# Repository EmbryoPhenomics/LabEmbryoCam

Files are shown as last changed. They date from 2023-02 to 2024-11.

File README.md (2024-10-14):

# LabEmbryoCam

This is the Github repository for the software that runs a LabEmbryoCam.

For more information about this technology, please visit: 

* User guides and background: www.phenomyx.co.uk 
* Hardware files: https://doi.org/10.5281/zenodo.13328175.



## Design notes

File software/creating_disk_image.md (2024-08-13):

# Guide for creating a new disk image

Download a raspbian lite image from the official website (https://www.raspberrypi.com/software/operating-systems/), latest version compatible with the LEC software is 32 or 64 bit BullsEye. 

Once you have flashed an SD card with a rapsbian lite image and completed the initial setup on a raspberry pi, follow the steps outlined here: https://github.com/TheMaroonHatHacker/gnomeforpi. This will set up Gnome on the raspbian OS, providing us a Gnome desktop environment and a virtual keyboard for use with the touchscreen that comes each LEC system. To enable the virtual keyboard, simply navigate to the accessibility settings and enable virtual keyboard.

Next, you can download the LEC software via the current GitHub repository, and subsequently you can install the required dependencies for the LEC software via `pip3 install -r requirements.txt`. Once this step has completed the image should be fully set up. 

To set up the desktop icon, please see `setup_desktop_icon.md` in this repository.

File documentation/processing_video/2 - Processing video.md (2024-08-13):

# 2 - Processing video produced by the LEC instrument

We provide a number of different scripts for viewing and processing the video produced by the LEC instrument:

### Viewers

- **examples/timepoint_viewer.py**
	A simple script for scrolling through video of a single timepoint from an individual subject.
- **examples/multi-timepoint_viewer.py**
	A script for viewing the first image from multiple videos of the same individual. 

### Processing

- **examples/compile_videos.py**
	Script to compile multiple videos of each individual into a single video file per individual.
- **examples/first_frame_compile.py**
	Script to retrieve the first frame of each video for each individual in your experiment, and compiling them into timelapse video files for each individual. 

*Note that these scripts are not a prerequisite for analysing your footage.*

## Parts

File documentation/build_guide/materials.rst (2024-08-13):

.. raw:: html

 <iframe src="https://plymouth222.autodesk360.com/shares/public/SH35dfcQT936092f0e43a8cc5597dfc66965?mode=embed" width="640" height="480" allowfullscreen="true" webkitallowfullscreen="true" mozallowfullscreen="true"  frameborder="0"></iframe>

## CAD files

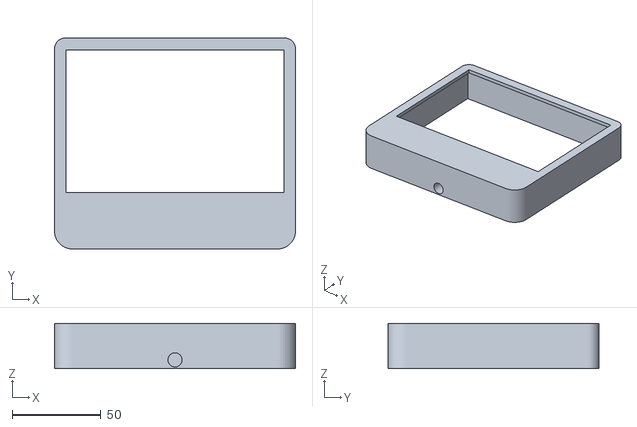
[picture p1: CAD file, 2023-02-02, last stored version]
hardware/STLs/humidification_chamber_main.stl
136.0 x 119.0 x 25.5

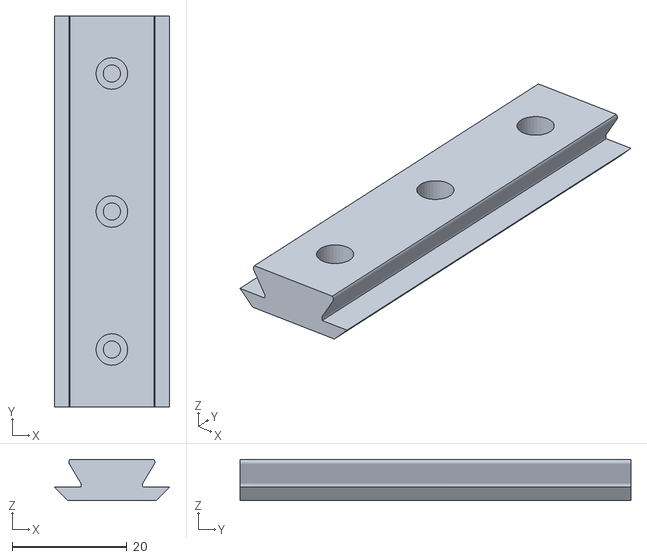
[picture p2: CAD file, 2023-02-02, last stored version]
hardware/STLs/z_carriage_assembly_light_insert.stl
20.0 x 68.0 x 7.16

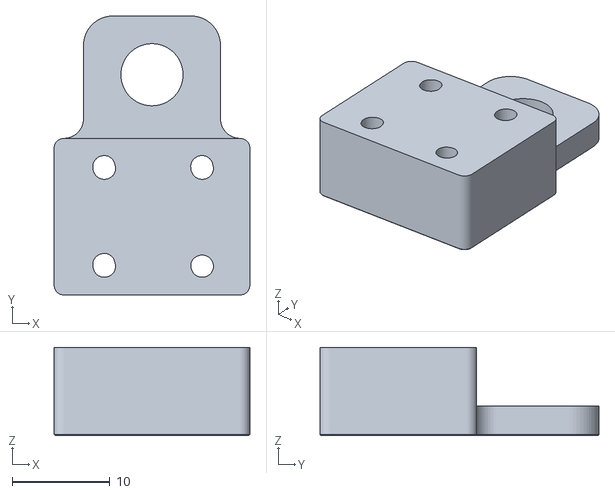
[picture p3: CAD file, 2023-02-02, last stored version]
hardware/STLs/z_carriage_assembly_camera_tripod_adapter.stl
20.0 x 28.5 x 9.00

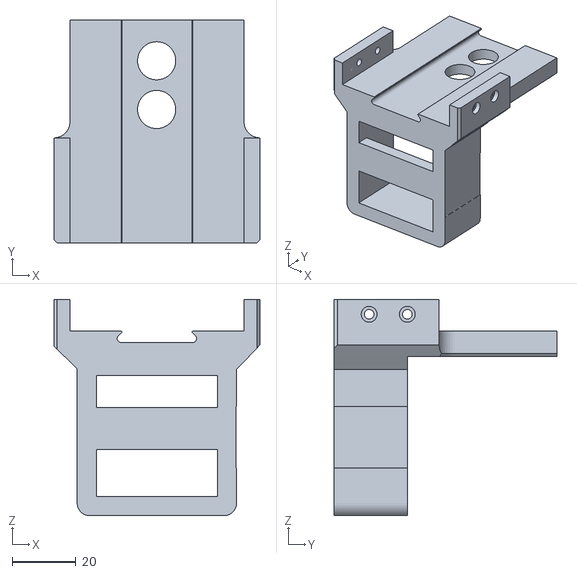
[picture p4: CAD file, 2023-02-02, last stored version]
hardware/STLs/z_carriage_assembly_camera_mount.stl
64.7 x 70.0 x 68.0

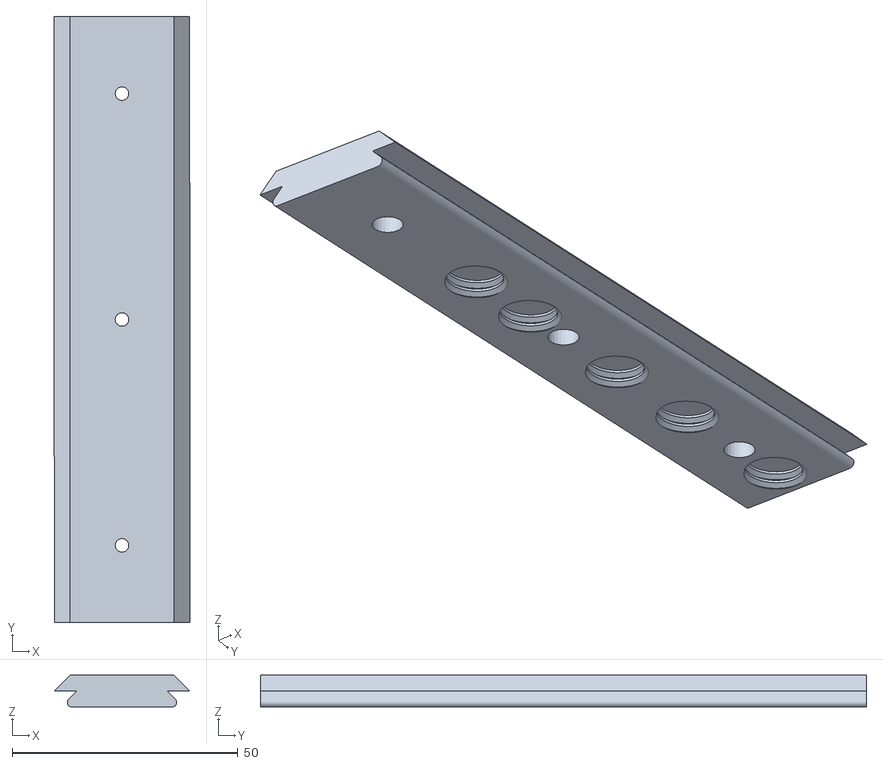
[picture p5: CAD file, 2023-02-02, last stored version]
hardware/STLs/z_carriage_assembly_optics_insert.stl
30.0 x 134.2 x 7.07

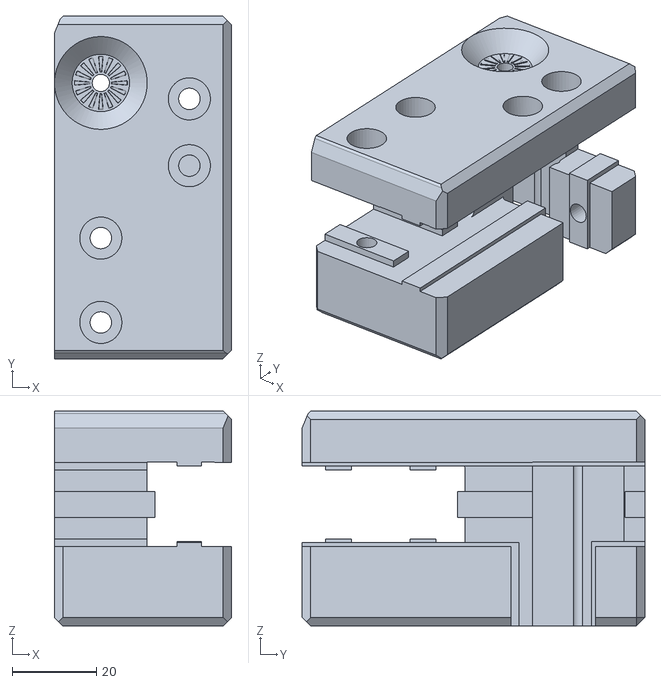
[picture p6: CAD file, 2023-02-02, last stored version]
hardware/STLs/back_motion_corner_mainbody_left.stl
42.0 x 81.3 x 51.0

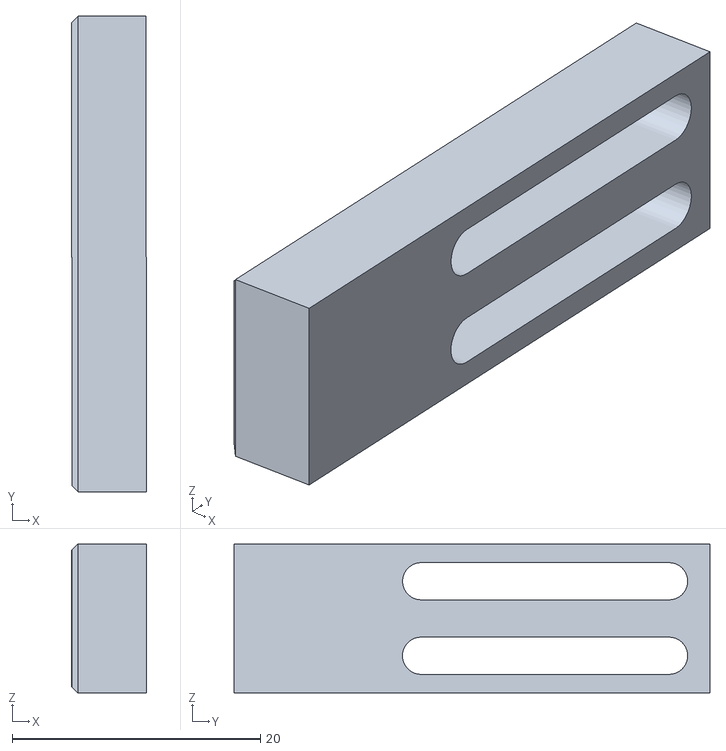
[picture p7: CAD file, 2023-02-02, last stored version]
hardware/STLs/z_carriage_assembly_limit_trigger.stl
6.00 x 38.3 x 12.0

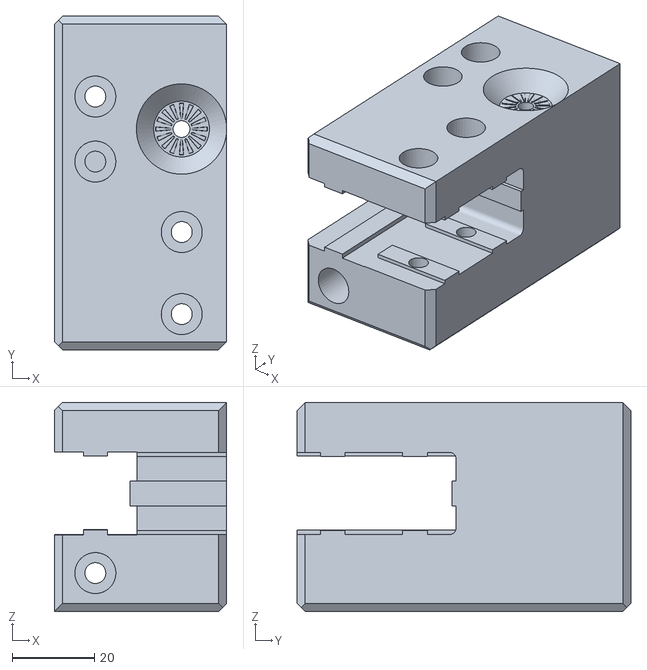
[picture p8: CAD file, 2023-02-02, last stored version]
hardware/STLs/back_motion_corner_mainbody_right.stl
42.0 x 81.4 x 51.0

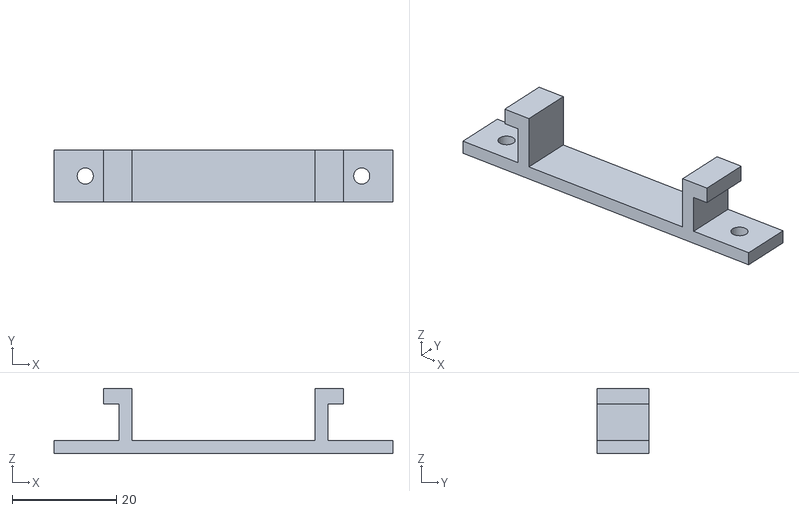
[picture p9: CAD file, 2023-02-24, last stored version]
hardware/STLs/cable vibration dampener bottom.stl
65.0 x 10.0 x 12.5

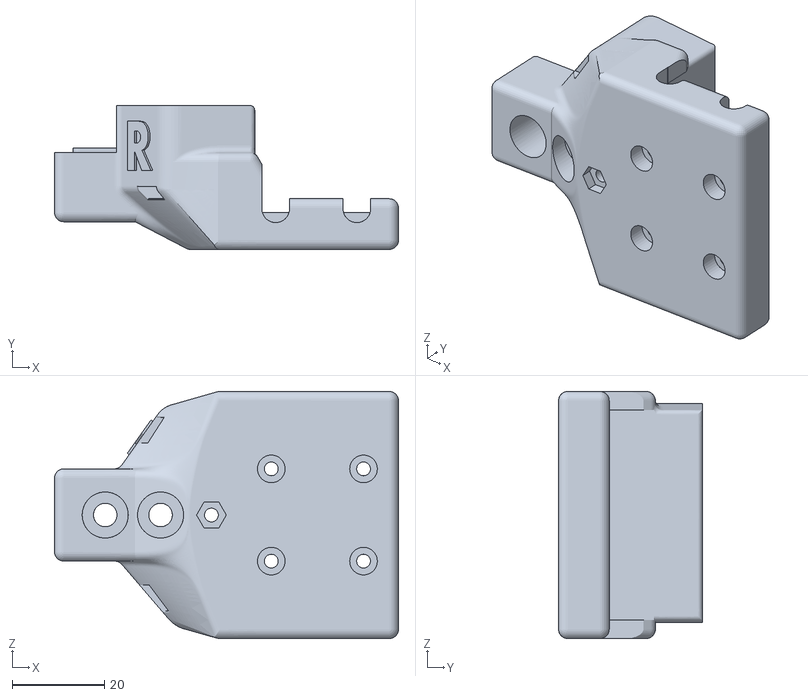
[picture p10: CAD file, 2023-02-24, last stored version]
hardware/STLs/y_mount_big_r.stl
74.6 x 31.2 x 53.6

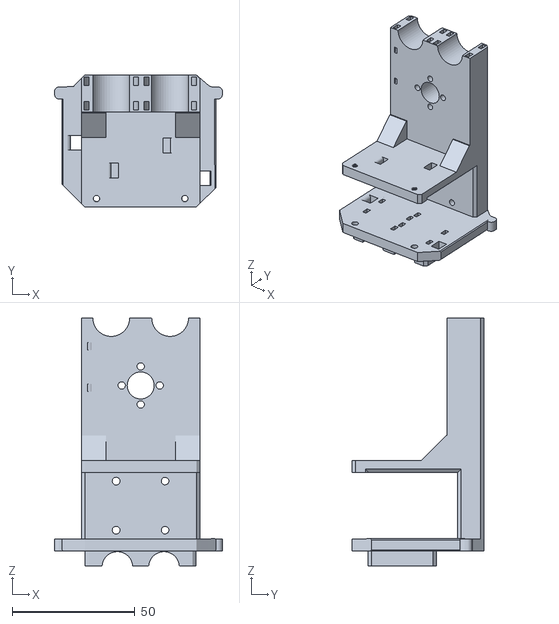
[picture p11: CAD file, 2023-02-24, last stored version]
hardware/STLs/z_carriage_rail_mount.stl
68.5 x 53.8 x 101.1

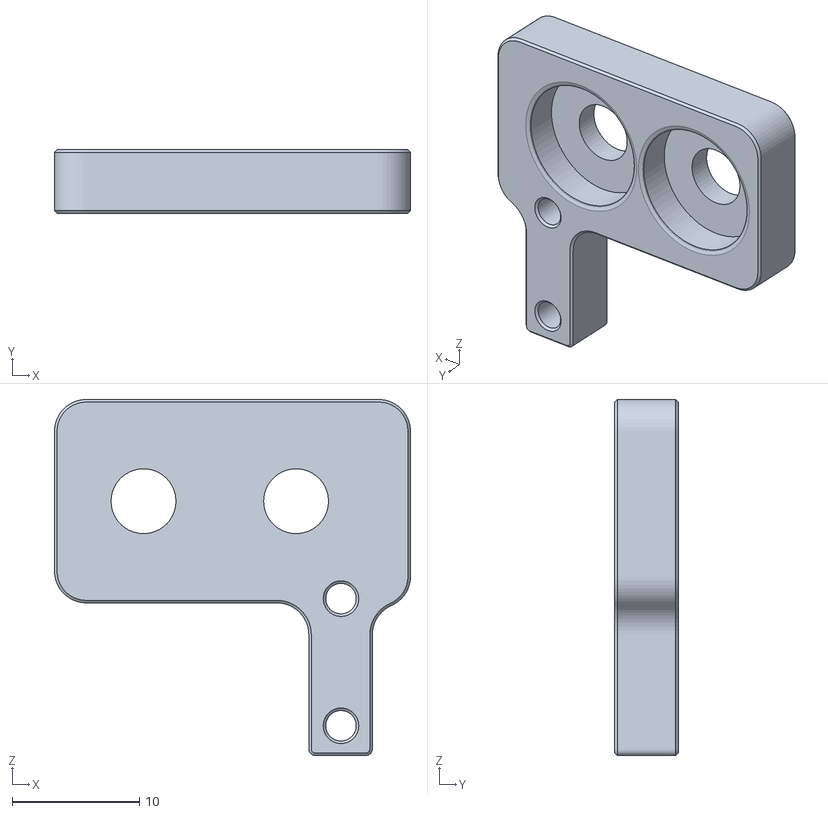
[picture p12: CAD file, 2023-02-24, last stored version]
hardware/STLs/y_mount_r_limit_switch_holder.stl
28.0 x 5.00 x 28.0

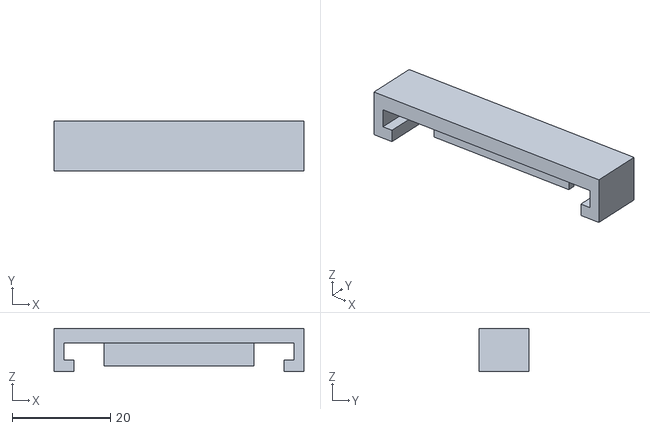
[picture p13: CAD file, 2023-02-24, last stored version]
hardware/STLs/cable vibration_dampener top.stl
51.0 x 10.2 x 8.80

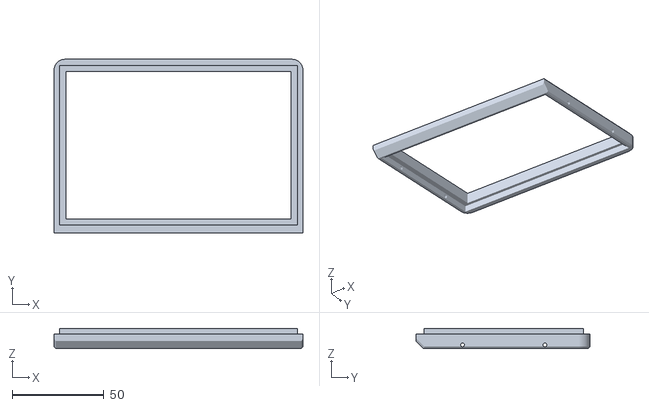
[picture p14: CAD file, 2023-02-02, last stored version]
hardware/STLs/humidification_chamber_lid.stl
136.0 x 94.8 x 11.0

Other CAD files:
hardware/STLs/y_mount_big_l.stl
hardware/STLs/z_carriage_light_carrier.stl
hardware/STLs/z_carriage_light_slider.stl
hardware/STLs/front_corner_left_bottom.stl
hardware/STLs/back_corner_knob(2).stl
hardware/STLs/back_motion_corner_left_smallbody.stl
hardware/STLs/back_motion_corner_right_smallbody.stl
hardware/STLs/bottom_corner_bracket(2).stl
hardware/STLs/bottom_corner_bracket_mirror(2).stl
hardware/STLs/electronics_SSD_mount.stl
hardware/STLs/electronics_atx_power_mount.stl
hardware/STLs/electronics_dual_arduino_mount_extended.stl
hardware/STLs/electronics_minitronics_fan fan_support(mirror)(2).stl
hardware/STLs/electronics_minitronics_fan support(2).stl
hardware/STLs/electronics_minitronics_mounting_bracket.stl
hardware/STLs/electronics_raspberry_pi_mount.stl
hardware/STLs/feet_leafspring(4).stl
hardware/STLs/front_corner_left_bottom_small.stl
hardware/STLs/front_corner_left_top.stl
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

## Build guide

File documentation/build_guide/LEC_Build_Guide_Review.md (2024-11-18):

# LabEmbryoCam Build Guide

**An opensource platform for automated measurement of developing animals**

***The LabEmbryoCam is a project originating with the EmbryoPhenomics research group at the University of Plymouth, UK. It has been made possible by support from UKRI, NERC, BBSRC and Plymouth Science Park***.

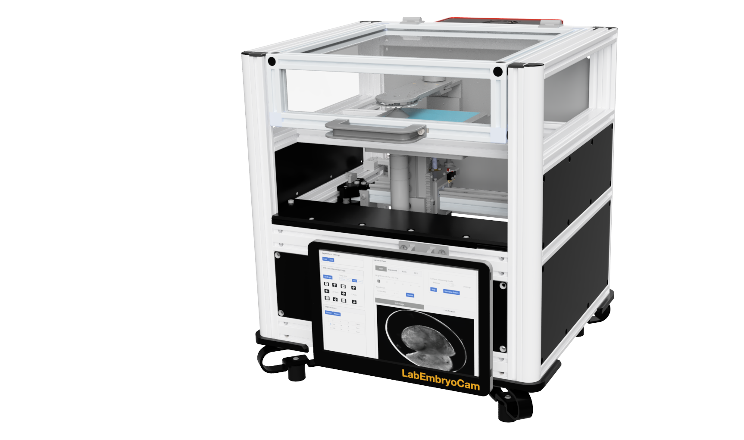
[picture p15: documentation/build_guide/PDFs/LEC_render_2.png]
Frame
 

-----------------
### 1.0 BACKGROUND
-----------------

The LabEmbryoCam provides:

* Automated movement of a camera and lighting in the X, Y and Z direction, over prolonged periods making it well suited to recording the process of embryonic development in aquatic animals.
* A custom user interface for easy setup of experiments, within a multiwell plate format, but also has sufficient flexibility for other culture formats - petri dishes, or even custom culture solutions.
* Incorporates an optional humifidification chamber to significantly reduce evaportation thereby solving one of the key challenges of long term timelapse imaging of aquatic animals.
* Vibration dampening addressing vibration, the enemy of timelapse imaging. 
* LabEmbryoCam incorporates sorbothene feet, 3D printed leafsprings and cable dampeners to minimise its effects on your imaging.
* A low cost, modular and versatile phenotyping platform taking advantage of 3D printed parts, single board computers, microcontrollers, stepper motors and lower cost cameras and lenses.
* Hackability this is an active project - if in doubt about any aspect of this instrument and its suitability to your activities, just ask.

**The LabEmbryoCam consists of both hardware and software, and the process of building both is described in the following series of pages.**

**Required Materials**

Building a LabEmbryoCam requires a range of mechnical and electrical parts, and 3D printed parts. 

* [**Components Required**](bom.md)

* [**Fixings required**](BOM_fixings.md)

The LabEmbryoCam is built using commonly available and low-cost consumer electronics, mechanical parts and 3D printed parts. Links and prices are provided as a guide, but prices vary and there is also significant scope for changing components, or suppliers due to availability, price, or user requirements.

A significant assortment of screws, nuts and washers are required to build a LabEmbryoCam (Bill of materials for fixings in **Required Materials**. To simplify the process of sourcing these parts, a kit of the required fixings can be bought here: https://www.modelfixings.co.uk/embryophenomics.htm (note this kit is not completely up-to-date)

To reduce the number of orders required to source these parts, parts are grouped to a few key suppliers and these are indicated in the bill of materials. Most parts are, however, available from a range of suppliers. There is considerable scope for changing parts to suit your use case.

A CAD model of the LabEmbryoCam is accessible here: https://a360.co/3ZnY7k5

## 1.1 Assembly Structure

The LabEmbryoCam project is organised as a range of different parts, and the numbering of parts indicates which assembly the part belongs to.

| **ASSEMBLY** | **DESCRIPTION**         |
| ---------- | ----------------------- |
| LEC_001    | Rexroth Aluminium Frame |
| LEC_002    | Bottom Corners          |
| LEC_003    | Back Corners            |
| LEC_004    | Front Corners           |
| LEC_005    | Y Carriage              |
| LEC_006    | X Carriage              |
| LEC_007    | Z Carriage              |
| LEC_008    | Electronics             |

## 1.2 Build Sequence

1. Frame
2. Back corners
3. Front corners
4. Y-carriage
5. X-carriage
6. Belts/Front top
7. Z-carriage
8. Bottom corners
9. Electronics
10. Panels

----------------

## 1.3 3D Printed Parts

STLs are the 3D model files, provided for producing the 3D printed parts. There are > 70 3D printed parts, with many requiring multiple copies. The (n) in the name of some parts indicates the number of that part that needs printing. For each section in this build guide, the required parts are listed. See the build guide for further information on 3D printing these parts.

Unless otherwise stated in **Specific Print Settings** parts should be printed using PETG with a minimum of 30 % infill, with 6 perimeters, 6 bottom layers and 6 top layers.

| Part                               | Quantity Needed | Specific Print Settings |
|------------------------------------|-----------------|-------------------------|
| LEC_002_P_01_FR/BL_BOTTOM-CORNER   | 2               |                         |
| LEC_002_P_01_FR/BR_BOTTOM-CORNER   | 2               |                         |
| LEC_002_P_03_LEAFSPRING            | 4               |                         |
| LEC_003_P_01_BACK-CORNER_L         | 1               |                         |
| LEC_003_P_02_BACK-CORNER_R         | 1               |                         |
| LEC_003_P_03_PULLEY_L              | 1               |                         |
| LEC_003_P_04_PULLEY_R              | 1               |                         |
| LEC_003_P_05_KNOB                  | 2               |                         |
| LEC_004_P_01_BOTTOM-CORNER_L       | 1               |                         |
| LEC_004_P_02_BOTTOM-CORNER_R       | 1               |                         |
| LEC_004_P_03_LOW-CORNER-BRACKET_L  | 1               |                         |
| LEC_005_P_01_YAXIS-LOWER_L         | 1               |                         |
| LEC_005_P_02_YAXIS-LOWER_R         | 1               |                         |
| LEC_005_P_03_YAXIS-UPPER_L         | 1               |                         |
| LEC_005_P_04_YAXIS-UPPER_R         | 1               |                         |
| LEC_005_P_05_YAXIS-LIMSWITCH_MOUNT | 1               |                         |
| LEC_006_P_01_Z-AXIS-CARRIAGE-UPPER | 1               | CF-PETG                 |
| LEC_007_P_03_TOP-CORNER_L          | 1               |                         |
| LEC_007_P_02_TOP-CORNER_R          | 1               |                         |
| LEC_006_P_02_Z-AXIS-CARRIAGE-LOWER | 1               | CF-PETG                 |
| LEC_008_P_01_Z-CARRIAGE            | 1               | CF-PETG                 |
| LEC_008_P_02_LIGHT-BRACKET-TOP     | 1               |                         |
| LEC_008_P_03_LIGHT-BRACKET-BOTTOM  | 1               |                         |
| LEC_008_P_04_OPTICS-MOUNT          | 1               | CF-PETG                 |
| LEC_008_P_05_CAM-MOUNT             | 1               | CF-PETG                 |
| LEC_008_P_06_RAIL-INSERT           | 1               | CF-PETG                 |
| LEC_008_P_07_OPTIC-SCREW           | 1               | CF-PETG                 |
| LEC_008_P_08_ZLIM-TRIGGER          | 1               |                         |
| LEC_008_P_09_BACK-ROD-SECURE       | 2               |                         |
| LEC_008_P_10_FRONT-ROD-SECURE      | 2               |                         |
| LEC_008_P_11_LIGHT-MOUNT           | 1               | CF-PETG                 |
| LEC_008_P_12_LIGHT-KNOB            | 1               | CF-PETG                 |
| LEC_008_P_13_LIGHT-DIFFUSER        | 1               | CF-PETG                 |
| LEC_009_P_01_MOUNTING-PLATE        | 1               |                         |

## 1.4 Fixings

The LabEmbryoCam is assembled using a number of fixings. These are listed in the table below, but in the build guide itself, they are split between the assembly sections.

| **Parts**                                         |**Quantity**|
|---------------------------------------------------|-------------|
| **M2.5**                                          |             |
| M2.5_10mm_SOCKETHEAD-SCREW                        | 6           |
| M2.5_10mm_BUTTONHEAD-SCREW                        | 4           |
| M2.5_12mm_BUTTONHEAD-SCREW                        | 4           |
| **M3**                                            |             | 
| M3_10mm_SOCKETHEAD-SCREW                          | 3           |
| M3_10mm_SUNKENHEAD-SCREW                          | 40          |
| M3_12mm_SOCKETHEAD-SCREW                          | 19          |
| M3_15mm_SOCKETHEAD-SCREW                          | 6           |
| M3_16mm_BUTTONHEAD-SCREW                          | 4           |
| M3_16mm_SOCKETHEAD-SCREW                          | 2           |
| M3_18mm_BUTTONHEAD-SCREW                          | 4           |
| M3_35mm_SOCKETHEAD-SCREW                          | 16          |
| M3_50mm SOCKETHEAD-SCREW                          | 2           |
| M3_HEX-NUT                                        | 20          |
| M3_SLIDE-NUT                                      | 40          |
| M3_WASHER                                         | 30          |
| **M4**                                            |             |
| M4_40mm_HEX-BOLT                                  | 2           |
| M4_HEX-NUT                                        | 2           |
| **M5**                                            |             |
| M5_10mm_BUTTONHEAD-SCREW                          | 20          |
| M5_10mm_SOCKETHEAD-SCREW                          | 9           |
| M5_14mm_SOCKETHEAD-SCREW                          | 2           | 
| M5_16mm_SOCKETHEAD-SCREW                          | 1           |
| M5_20mm_BUTTONHEAD-SCREW                          | 2           |
| M5_HEX-NUT                                        | 2           |
| M5_SLIDE-NUT                                      | 42          |
| **M6**                                            |             |
| M6_12mm_BUTTONHEAD-SCREW                          | 4           |
| M6_45mm_BUTTONHEAD-SCREW                          | 4           |
| M6_HEX-NUT                                        | 4           |
| **Other**                                         |             |
| FAST-CONNECTOR-SCREW                              | 56          |
| FAST-CONNECTOR-SLIDE-PIN                          | 56          |
| END-RAIL-COVER                                    | 4           |
| END-RAIL-COVER-ROUNDED                            | 4           |
| PANEL-FIXINGS                                     | 44          |
| CABLE-TIE-3mm                                     | 4           |
| CABLE-TIE-5mm                                     | 8           |

## 1.5 Components

The LabEmbryoCam is built using an array of components - in most instances, these are readily available online and not custom. The two exceptions are i) the IGUS rails are cut to 250 mm length and this can have a short leadtime (one week typically), and ii) the electronics enclosure has custom machined panels for the ports, and PCB mountings. 

All required components are listed in the table below, and are organised by the different assemblies.

| **Parts**                                         |**Quantity**|
|---------------------------------------------------|-------------|
| LEC_002_C_01_SORBOTHENE-FEET                      | 4           |
| LEC_003_C_01_F623ZZ-BEARING                       | 4           |
| LEC_004_C_01_F623ZZ-BEARING                       | 8           | 
| LEC_004_C_02_XY-STEPPER                           | 2           |
| LEC_004_C_03_TIMING-PULLEY                        | 2           |
| LEC_005_C_01_YAXIS-CARRIAGE_L                     | 1           |
| LEC_005_C_02_YAXIS-CARRIAGE_R                     | 1           |
| LEC_005_C_03_YAXIS-RAIL_L                         | 1           |
| LEC_005_C_04_YAXIS-RAIL_R                         | 1           |
| LEC_005_C_F623ZZ-BEARING                          | 8           |
| LEC_006_C_01_Z-AXIS-RAIL-UPPER                    | 1           |
| LEC_006_C_02_Z-AXIS-RAIL-LOWER                    | 1           |
| LEC_006_C_03_Z-AXIS-RAIL-CARRIAGE-LOWER           | 1           |
| LEC_006_C_04_Z-AXIS-RAIL-CARRIAGE-UPPER           | 1           |
| LEC_006_C_05_LEADSCREW-NUT                        | 1           |
| LEC_006_C_06_LINEAR-BEARING                       | 4           |
| LEC_006_C_07_LIM-SWITCH                           | 1           |
| LEC_007_C_GT2-BELT                                | 1           |
| LEC_008_C_01_Z-STEPPER                            | 1           |
| LEC_008_C_02_CAM                                  | 1           |
| LEC_008_C_03_LENS                                 | 1           |
| LEC_008_C_04_KFL08                                | 1           |
| LEC_008_C_05_FLEX-COUPLING                        | 1           |
| LEC_008_C_06_Z-SCREW                              | 1           |
| LEC_008_C_07_F-ROD                                | 2           |
| LEC_008_C_08_R-ROD                                | 2           |
| LEC_008_C_09_LED-RING                             | 1           |
| LEC_009_C_01_THOR-CUST-BASE-PLATE                 | 1           |
| LEC_009_C_02_THOR-CUST-PORT-PLATE                 | 1           |
| LEC_009_C_03_THOR-CUST-FAN-PLATE                  | 1           |
| LEC_009_C_04_THOR_EC2030BR                        | 1           |
| LEC_009_C_05_RPI4                                 | 1           |
| LEC_009_C_06_USB-HUB                              | 1           |
| LEC_009_C_07_PSU-SEASONIC300SUG                   | 1           |
| LEC_009_C_08_DUET                                 | 1           |
| LEC_009_C_09_ARDUINO                              | 1           |
| LEC_009_C_10_RJ45-CONN                            | 1           |
| LEC_009_C_11_SWITCH                               | 1           |
| LEC_009_C_12_HDMI-CONN                            | 2           |
| LEC_009_C_13_USB-CONN                             | 2           |
| LEC_009_C_14_DB15-M-CONN                          | 1           |
| LEC_009_C_15_DB25-M-CONN                          | 1           |
| LEC_009_C_16_ATX-BREAKOUT                         | 1           |
| LEC_009_C_17_FAN                                  | 1           |

## 1.6 CAD

The LabEmbryoCam is modelled using the CAD software Autodesk Fusion360 - freely availabile for hobbyist use, or with an educational license. 

***INTERACTIVE AND DOWNLOADABLE CAD MODEL***: https://a360.co/3ZnY7k5

--------

-----------------
### 2.0 ASSEMBLY
-----------------

-----------------
### 3.0 ALUMINIUM EXTRUSION FRAME
-----------------

***The LabEmbryoCam frame is constructed using aluminium extrusion of different cross-sections and lengths. Aluminium extrusion is aluminium of a shape that enable fixing parts to be connected, for connecting extrusion together, or for attaching parts to the extrusion. Here we use Bosch Rexroth extrusion and the accompanying fast connectors to build the frame.***

| **Parts** | **Shorthand Name **                   |**Quantity**|
|-----------|----------------------------------------|-------------|
| ***Extrusion*** |                                  |             |
| LEC_001_E_01_2040-EXTRUSION-356MM | 2040-356MM     | 8           |
| LEC_001_E_02_2040-EXTRUSION-336MM | 2040-336MM     | 2           |
| LEC_001_E_03_2020-EXTRUSION-418MM-ROUNDED | 2020-418MM-ROUNDED | 2 |
| LEC_001_E_04_2020-EXTRUSION-416MM | 2020-416MM     | 4           |
| LEC_001_E_05_2020-EXTRUSION-356MM | 2020-356MM     | 2           |
| ***Fixings*** |                                    |             |
| LEC_001_F_01_FAST-CONNECTOR-SCREW | FAST-CONNECTOR-SCREW | 56     |
| LEC_001_F_02_FAST-CONNECTOR-SLIDE-PIN | FAST-CONNECTOR-SLIDE-PIN |56|
| LEC_001_F_03_2020-END-COVER | 2020-END-COVER        | 4           |
| LEC_001_F_04_2020-ROUNDED-END-COVER | 2020-ROUNDED-END-COVER | 4  |
| LEC_001_F_05_PANEL-FIXINGS | PANEL-FIXINGS          | 44          |
| LEC_002_F_01_M5-10MM-BUTTONHEAD-SCREW | M5-10MM-BUTTONHEAD-SCREW | 12 |
| LEC_002_F_02_M5-SLIDE-NUT             | M5_SLIDE-NUT             | 12 |  | ***3D Printedd*** |                                    |             |
| LEC_002_P_01_FR/BL_BOTTOM-CORNER      | FR/BL_BOTTOM-CORNER      | 2  |
| LEC_002_P_01_FR/BR_BOTTOM-CORNER      | FR/BR_BOTTOM-CORNER      | 2  |

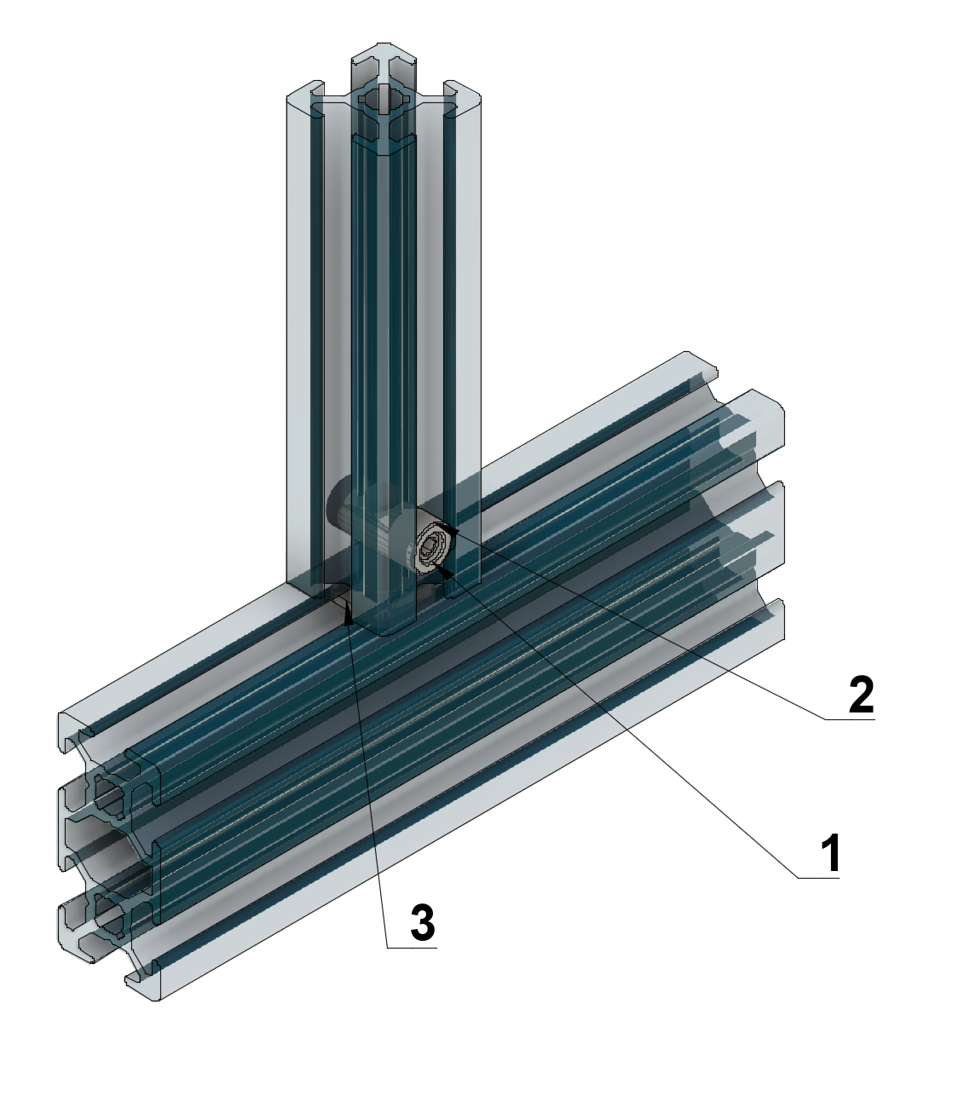
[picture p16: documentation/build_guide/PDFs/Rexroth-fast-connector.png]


**FIGURE 3.0 Connecting lengths of aluminium extrusion together**. **Fast connector screw** (1 and 2), used to tighten into the **fast connector slide pin** (3). 

** ****

***In the guide we refer to 2020 extrusion, which is 20 mm x 20 mm in cross section, whereas 2040 extrusion is 20 mm x 40 mm in cross section. 2020 extrusion with a rounded corner is also used on each outer upright corner of the instrument.***. 



**FIGURE 3.2 Frame design**. 

**3.1** Start by constructing the rear of the frame (2 x **2040-336mm-RAIL**, 2 x **2020-416mm-RAIL**. Take each **2020-416mm-RAIL**, and into the inside groove slide in 4 **FAST-CONNECTOR-SLIDE-PIN** into each rail. Insert the **FAST-CONNECTOR-SCREW** into each **2040-336mm-RAIL**, move these in position following the diagram in Figure 2, and then tighten each screw using the 3mm allen key. 

**3.2**Then add the horizontal rails into this rear frame (8 x **2040-356mm-RAIL**, 2 x **2020-418mm-ROUNDED-RAIL**). Lie down the assembled rear frame on the back face and then insert 4 **FAST-CONNECTOR-SLIDE-PIN** into the upward facing grooves. Insert the **FAST-CONNECTOR-SCREW** into each **2040-356mm-RAIL**, and insert these rails into the **FAST-CONNECTOR-SLIDE-PIN**. Do not tighten the allen keys at this stage, otherwise you will be unable to carry out the following steps. Insert 2 **FAST-CONNECTOR-SLIDE-PIN** into each **2020-418mm-ROUNDED-RAIL**. Insert the **2020-418mm-ROUNDED-RAIL** inline with the rear **2020-416mm-RAIL**. The spacing of each of the horizontal **2040-356mm-RAIL** must be established to fit each of the side panels. Use each of the side panels to adjust the spacing of these rails. Once all of these are in place, tighten all screws using the 3mm allen key.

**3.3**Take each of the **2020-356mm-RAIL** and insert the **FAST-CONNECTOR-SCREW**. Then insert each of the **FAST-CONNECTOR-SLIDE-PIN** into the ends of the **2020-356mm-RAIL**. The **2020-356mm-RAIL** used to mount the humidification chamber must be inserted so that the fast connectors are facing horizontally, i.e. the screws used to tighten the fast connectors are facing forwards, not upwards. This means there is then space at the end of each of these rails to attach the humidification chamber. Make sure to orient the slide pins so that the grooves are in line with the **FAST-CONNECTOR-SCREW**. Slide the rails and the **FAST-CONNECTOR-SLIDE-PIN** into the 2nd from the top **2040-356mm-RAIL**. Do not tighten these screws as they will have to be aligned with the humidification chamber mounts later in the build. 

**3.4**Next, assemble the front of the frame. Take the remaining 2 x **2020-416mm-RAIL** and insert 2 **FAST-CONNECTOR-SLIDE-PIN** into the inward facing grooves on each rail. Inset the **FAST-CONNECTOR-SCREW** into the 2 remaining **2040-336mm-RAIL**,  and assemble these as per the diagram. Again, use the front panel to adjust the spacing between the top and bottom **2040-336mm-RAIL**. Insert **FAST-CONNECTOR-SCREW** and **FAST-CONNECTOR-SLIDE-PIN** into the ends of each of the horizontal **2040-356mm-RAIL**. Then slide in the assembled front rails into **FAST-CONNECTOR-SLIDE-PIN** in the horizontal **2040-356mm-RAIL**. Do no tighten the screws. Finally, slide into place the 2 remaining **2020-418mm-ROUNDED-RAIL** alongside the front frame. Once all are in place, tighten the **FAST-CONNECTOR-SCREW** using the 3mm allen key. 

**3.5** To finish, insert the plastic end rail covers (4 x **END-RAIL-COVER** and 4 x **END-RAIL-COVER-ROUNDED**). **PANEL-FIXINGS** can then be added to each of the railings. These are added on the underside and bottom of the **2040-356mm-RAIL** and **2040-336mm-RAIL**, and can be spaced out using the complementary panels. Do not fix the panels yet as they will get in the way of subsequent steps.

-----------------
### 4.0 BACK CORNERS
-----------------

***The back corners are central to effective routing of the belts that create X and Y movement of the instrument. The knobs at the rear of the back corner contribute to this functioning by allowing adjustment of the tension of each of the two belts in the instrument.***

| **Parts** | **Shorthand Name**                     |**QUANTITY**|
|-----------|----------------------------------------|-------------|
| ***Printed*** |                                    |             |
| LEC_003_P_01_BACK-CORNER_L | BACK-CORNER_L         | 1           |
| LEC_003_P_02_BACK-CORNER_R | BACK-CORNER_R         | 1           |
| LEC_003_P_03_PULLEY_L | PULLEY-L                  | 1           |
| LEC_003_P_04_PULLEY_R | PULLEY-R                  | 1           |
| LEC_003_P_05_KNOB | KNOB                           | 2           |
| ***Components*** |                                 |             |
| LEC_003_C_01_F623ZZ-BEARING | F623ZZ-BEARING       | 4           |
| ***Fixings*** |                                    |             |
| LEC_003_F_01_M3-16MM_SOCKETHEAD-SCREW | M3-16mm_SOCKETHEAD-SCREW | 2|
| LEC_003_F_02_M3-WASHER | M3-WASHER                | 6           |
| LEC_003_F_03_M4-40MM_HEX-BOLT | M4-40MM_HEX-BOLT  | 2           |
| LEC_003_F_04_M4-HEX-NUT | M4-HEX-NUT              | 2           |
| LEC_003_F_05_M5-10MM_BUTTONHEAD-SCREW | M5-10MM_BUTTONHEAD-SCREW | 8|
| LEC_003_F_06_M5-SLIDE-NUT | M5-SLIDE-NUT        | 8           |

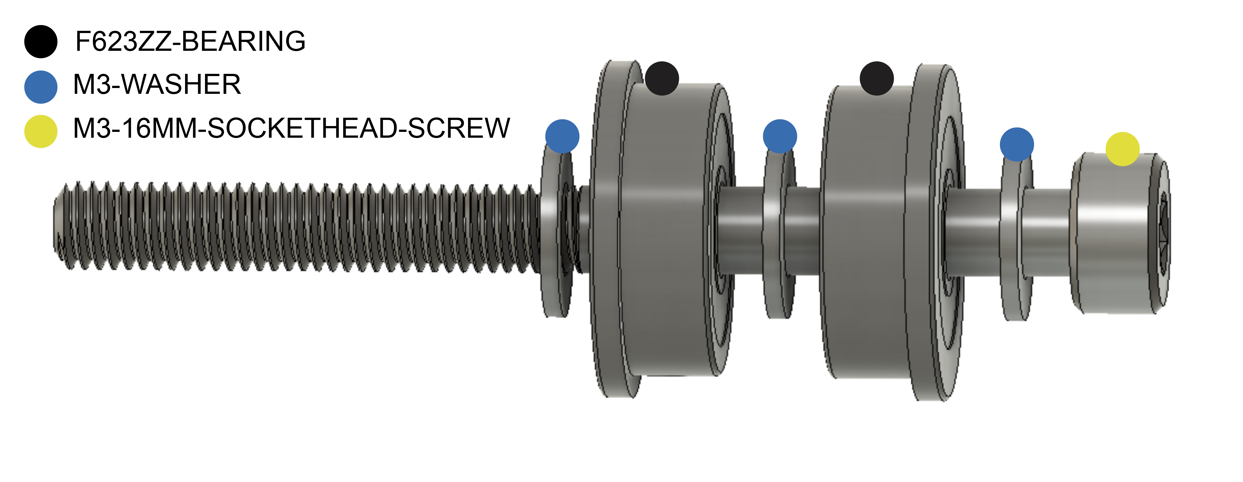
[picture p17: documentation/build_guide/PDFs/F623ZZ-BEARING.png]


**FIGURE 4.0 FIGURE**

**4.1** The back corners of the LECs are used to feed through the belts, and to adjust the tension of these. Start by constructing each of the rear tensioners, and the associated tensioner knobs. Into the **PULLEY_L** and **PULLEY_R**, screw in the **M4_40mm_HEX-BOLT** so that the thread is sticking out of the back. Next, screw in the **M3_16mm_SOCKETHEAD-SCREWS** into just the base of each and screw each of the components into the inside of the pulleys in this order: **M3_WASHER**, **F623ZZ-BEARING**, **M3_WASHER**, **F623ZZ-BEARING**, **M3_WASHER**. 

**4.2.** Next, we need to attach the **BACK-CORNER_L** and **BACK-CORNER_R**. Start by adding the **M5_SLIDE-NUTS** into the frame. For each side, add 2 **M5_SLIDE-NUTS** into the inside top groove of the **2040-356mm-RAIL** that is 2nd from the bottom, and 2 **M5_SLIDE-NUTS** to the back of the **2020-416mm-RAIL**. Then fix the **BACK_CORNER_L** and **BACK_CORNER_R** in place. Line up the **M5_SLIDE-NUTS** inline with the screw holes on each 3D printed part, and screw these place using the **M5_10mm_BUTTONHEAD-SCREWS**. 

**4.3** Finally, push each of the assembled pulleys into the groove of the **BACK-CORNER_L** and **BACK-CORNER_R** so that the thread of the **M4_40mm_HEX-BOLTS** is coming out of the back of the machine. Insert **M4_HEX-NUTS** into the groove at the rear of the **KNOB**, and then loosely screw on each of the knobs to the thread of the **M4_40mm_HEX-BOLTS**. 

-----------------
### 5.0 FRONT CORNERS
-----------------

***The front corners are complex parts that are crucial for effective functioning of the instrument. The belts must follow the outlined routes, and in the correct orientation, for the LEC to work as it should.***

| **Parts** | **Shorthand name**                    |**QUANTITY** |
|-----------|----------------------------------------|-------------|
| ***Printed*** |                                    |             |
| LEC_004_P_01_BOTTOM-FRONT-CORNER-LEFT | BOTTOM-CORNER-L     | 1|
| LEC_004_P_02_BOTTOM-FRONT-CORNER-RIGHT | BOTTOM-CORNER-R     |1|
| LEC_004_P_03_TOP-FRONT-CORNER-LEFT | TOP-CORNER-L | 1     |
| LEC_004_P_04_TOP-FRONT-CORNER-RIGHT | TOP-CORNER-R | 1     |
| LEC_004_P_05_BOTTOM-SMALL-LEFT-BRACKET | BOTTOM-SMALL-L | 1     |
| ***Components*** |                                 |             |
| LEC_004_C_01_F623ZZ-BEARING | F623ZZ-BEARING        | 12           |
| LEC_004_C_02_XY-STEPPER | XY-STEPPER                | 2           |
| LEC_004_C_03_TIMING-PULLEY | TIMING-PULLEY          | 2           |
| ***Fixings*** |                                     |             |
| LEC_004_F_01_M3-15MM-SOCKETHEAD-SCREW | M3-15MM-SOCKETHEAD-SCREW | 6|
| LEC_004_F_02_M3-35MM-SOCKETHEAD-SCREW | M3-35MM-SOCKETHEAD-SCREW | 6|
| LEC_004_F_06_M3-40MM-BUTTONHEAD-SCREW | M3-40MM-BUTTONHEAD-SCREW | 4|
| LEC_004_F_03_M3-WASHER | M3-WASHER                  | 18          |
| LEC_004_F_04_M3-HEX-NUT | M3-HEX-NUT                   | 6           |
| LEC_004_F_05_M5-10MM-SOCKETHEAD-SCREW | M5-10MM-SOCKETHEAD-SCREW | 2|
| LEC_004_F_06_M5-20MM-BUTTONHEAD-SCREW | M5-20MM-BUTTONHEAD-SCREW | 2|
| LEC_004_F_07_M5-SLIDE-NUT | M5-SLIDE-NUT             | 8          |

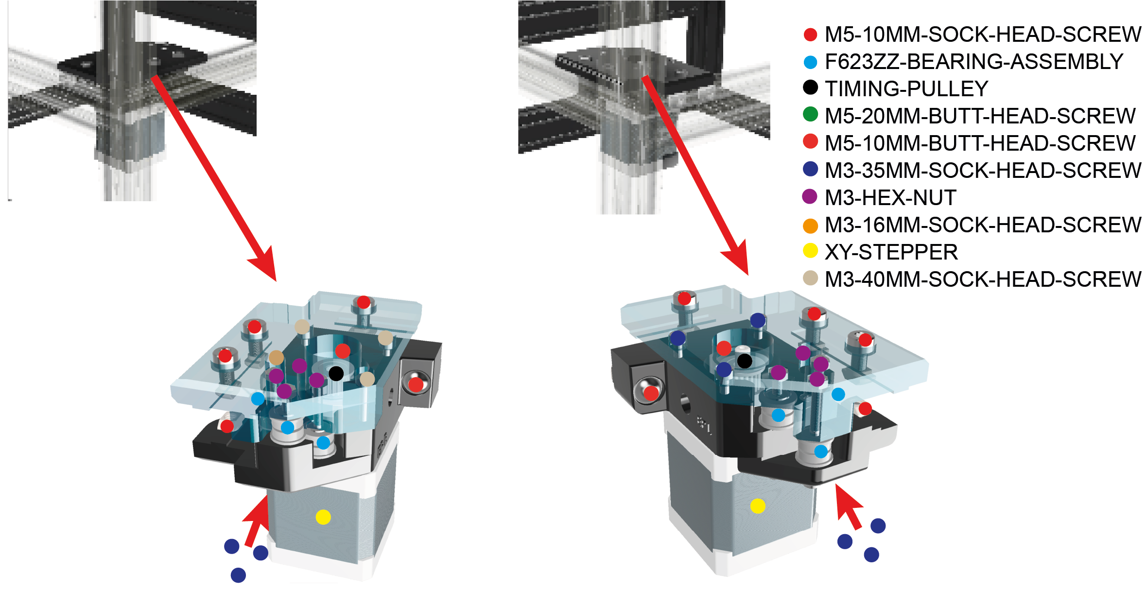
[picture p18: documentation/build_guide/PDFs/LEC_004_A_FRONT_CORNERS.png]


**FIGURE 5.0. Front corners, with the **

**5.1.** The front corners are used to route the XY belts through the stepper motors. Start by adding the **BOTTOM-CORNER_L**, **BOTTOM-CORNER_R** and **LOW-CORNER-BRACKET_L** to the front corners of the frame. These are attached using **M5_10mm_SOCKETHEAD-SCREW**,  **M5_20mm_BUTTONHEAD-SCREW** and **M5_SLIDE-NUT**. To attach these, screw each of the screws in place, and loosely screw the slide nuts onto the thread of these. Push the entire piece into place in the frame and then tighten the screws using an allen key. 

**5.2.** Next, we need to assemble the bearings and stepper motors used to route the belts into the bottom front corner pieces. Start by attaching each of the **XY-STEPPER** to the bottom corner pieces. When viewed from the top, this will mean screwing a **M3_15mm_SOCKETHEAD-SCREW** into the top left and top right of the left and right bottom corner pieces, and **XY-STEPPER** screw holes respectively. Leave the **XY-STEPPER** attached by the single screw. 

**5.3.** Next, screw in 3 **M3_35mm_SOCKETHEAD-SCREW** into the underside of the **BOTTOM-CORNER_L** and **BOTTOM-CORNER_R**. Screw these in leaving approximately 12mm of thread facing vertically out of bottom corner pieces. Onto each of these threads, add these fixings in this order: **M3_WASHER**, **F623ZZ-BEARING**, **M3_WASHER**, **F623ZZ-BEARING**, **M3_WASHER**. Then, to the thread of the stepper motor, add the **TIMING-PULLEY**. The top of the timing pulleys should be at approximately the same height as the bottom corner pieces, and are screwed in place using an allen key. 

**5.4.** The top corner pieces are left out at this point, as we must assemble other components (**LEC_005_A_Y-CARRIAGE**, **LEC_006_A_X-CARRIAGE**, **LEC_007_A_BELTS**) first. 

-----------------
### 6.0 Y-AXIS
-----------------

***The y-carriage is responsible for front to back movement of the instrument. It relies on two linear rails mounted on either side of the instrument. Proper mounting of these two linear rails is important to prevent binding of the instrument during movements along the y-axis.***

| **Parts** | **Shorthand Name **                    |**QUANTITY**|
|-----------|----------------------------------------|-------------|
| ***Printed*** |                                    |             |
| LEC_005_P_01_YAXIS-LOWER | YAXIS-LOWER         | 2           |
| LEC_005_P_02_YAXIS-UPPER | YAXIS-UPPER         | 2           |
| LEC_005_P_03_YAXIS-LIMSWITCH-MOUNT | YAXIS-LIMSWITCH-MOUNT | 1   |
| LEC_005_P_04_YAXIS-LIM-TRIG | YAXIS-LIMIT-TRIGGER | 1   |
| ***Components*** |                                  |             |
| LEC_005_C_01_YAXIS-CARRIAGE-L | YAXIS-CARRIAGE-L    | 1           |
| LEC_005_C_02_YAXIS-CARRIAGE-R | YAXIS-CARRIAGE-R    | 1           |
| LEC_005_C_03_YAXIS-RAIL-L | YAXIS-RAIL-L            | 1           |
| LEC_005_C_04_YAXIS-RAIL-R | YAXIS-RAIL-R            | 1           |
| LEC_005_C_05_F623ZZ-BEARING | F623ZZ-BEARING           | 8           |
| ***Fixings*** |                                     |             |
| LEC_005_F_01_M3_10MM-SOCKETHEAD-SCREW | M3-10MM-SOCKETHEAD-SCREW| 20|
| LEC_005_F_02_M3_12MM-SOCKETHEAD-SCREW | M3-12MM-SOCKETHEAD-SCREW| 8 |
| LEC_005_F_03_M3_35MM-SOCKETHEAD-SCREW | M3-35MM-SOCKETHEAD-SCREW| 4 |
| LEC_005_F_04_M3_50MM-SOCKETHEAD-SCREW | M3-50MM-SOCKETHEAD-SCREW| 1 |
| LEC_005_F_04_M3_60MM-SOCKETHEAD-SCREW | M3-60MM-SOCKETHEAD-SCREW| 1 |
| LEC_005_F_05_M3_WASHER | M3_WASHER                  | 12          |
| LEC_005_F_06_M3_HEX-NUT | M3_HEX-NUT                | 2           |
| LEC_005_F_07_M3_SLIDE-NUT | M3_SLIDE-NUT            | 20          |
| LEC_005_F_08_M5_10MM-SOCKETHEAD-SCREW | M5-10MM-SOCKETHEAD-SCREW | 3 |
| LEC_005_F_09_M5_14MM-SOCKETHEAD-SCREW | M5-14MM-SOCKETHEAD-SCREW | 2 |
| LEC_005_F_10_M5_16MM-SOCKETHEAD-SCREW | M5-16MM-SOCKETHEAD-SCREW | 1 |
| LEC_005_F_11_M5_SLIDE-NUT | M5_SLIDE-NUT            | 8           |

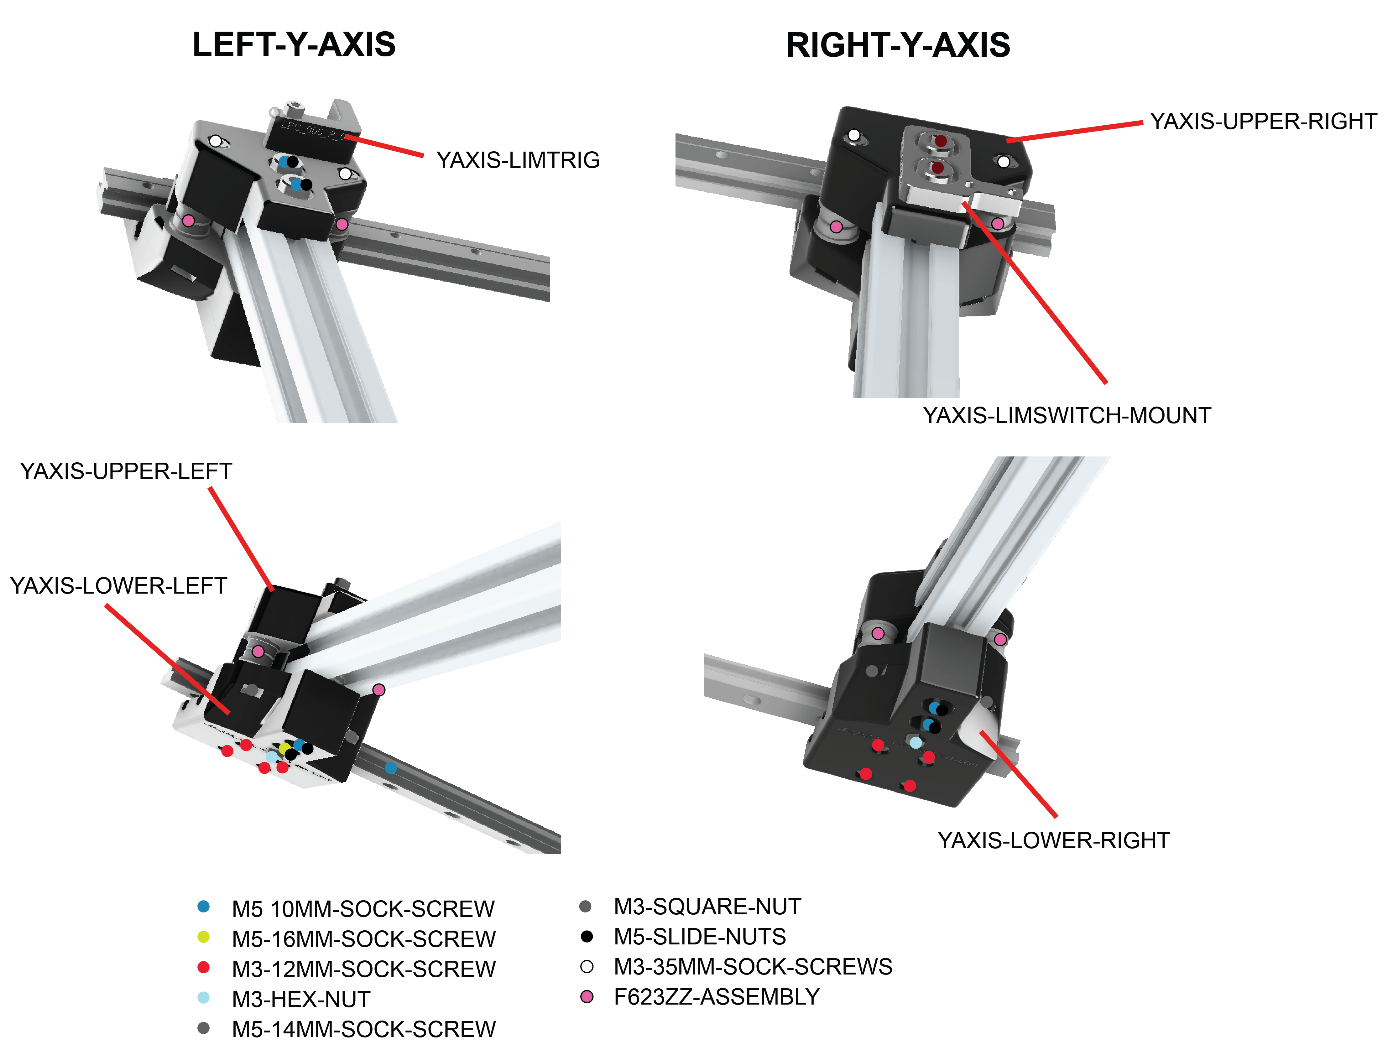
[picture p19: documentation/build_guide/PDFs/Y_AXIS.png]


**FIGURE 6.0**

**6.1**. Now, the Y-carriage components need to be added to the frame. Take both the **YAXIS-RAIL_L** and **YAXIS-RAIL_R** and slide on the **YAXIS-CARRIAGE_L** and **YAXIS-CARRIAGE_R** to the end of each of these. 

**6.2.** Attach the **YAXIS-LOWER_L** and **YAXIS-LOWER_R** to the **YAXIS-CARRIAGE_L** and **YAXIS-CARRIAGE_R** respectively, using **M3_12mm_SOCKETHEAD-SCREW**. Into both the **YAXIS-LOWER_L** and **YAXIS-LOWER_R**, screw in **M5_10mm_SOCKETHEAD-SCREW** and **M5_16mm_SOCKETHEAD-SCREW**, and loosely screw on **M5_SLIDE-NUT** to the ends of these. 

**6.3** To attach these to the frame, insert **10mm_COUNTERSUNK-SCREW** into each of the rails, and loosely screw on **M3_SLIDE-NUT** to the threads of these. Insert the assembled rails and slide nuts into the grooves on the underside of the horizontal rails inbetween the front and back corner 3D printed parts. Make sure to push these up against the front corner pieces, and then using an allen key screw these into place. Once attached, the assembled carriages should move freely along the rails. 

**6.4** Next, construct the complimentary upper sections to the carriages. Take the **YAXIS-LIMSWITCH_MOUNT** and screw it into the **YAXIS-UPPER_L** using **M5_14mm_SOCKETHEAD-SCREW**. Then loosely screw on **M5_SLIDE-NUT** to the threads of these. Next, partically screw in **M3_35mm_SOCKETHEAD-SCREW**, so that the threads of the outer two screws are protruding equidistant with the height of the **YAXIS-LOWER_L**, and so the central is not protruding at all. Onto the threads of the outside two **M3_35mm_SOCKETHEAD-SCREW**, add these fixings in this order: **M3_WASHER**, **F623ZZ-BEARING**, **M3_WASHER**, **F623ZZ-BEARING**, **M3_WASHER**. 

**6.5** For the **YAXIS-UPPER_R**, these steps are slightly different. Screw in **M3_10mm_COUNTERSUNK-SCREW**, and loosely screw on **M5_SLIDE-NUT** to the threads of these. Next, take the **YAXIS-LIMTRIG** and screw this partically into the **YAXIS-UPPER_R** using **M3_50mm SOCKETHEAD-SCREW**, so that the thread does not protrude from the opposite hole. Screw in two more **M3_35mm_SOCKETHEAD-SCREW** either side of this, and assembled the fixings as per step **18**.  

**6.6** You should be left with 2 main assembled complimentary upper parts from steps **18** and **19**. Leave these to one side for now, we will attach these once the X-carriage in the next section has been assembled. 

-----------------
### 7.0 X-AXIS
-----------------

*** The x-carriage is the point of attachment for each end of the two belts responsible for X and Y motion. It slides from side to side on the linear rail attached to the 2020 piece of extrusion that creates the y-carriage.***

| **Parts** | **Shorthand Name**                     |**QUANTITY**|
|-----------|----------------------------------------|-------------|
| ***Extrusion*** |                                  |             |
| LEC_006_E_01_2020-318MM | 2020-318MM     | 1           |
| ***Printed*** |                                    |             |
| LEC_006_P_01_X-AXIS-CARRIAGE | Z-AXIS-CARRIAGE | 1   |
| ***Components*** Z|                                |             |
| LEC_006_C_01_X-AXIS-WS-RAIL | X-AXIS-WS-RAIL  | 1           |
| LEC_006_C_02_X-AXIS-WS-CARRIAGE | X-AXIS-WS-CARRIAGE  | 1           |
| LEC_006_C_03_LEADSCREW-NUT | LEADSCREW-NUT          | 1           |
| LEC_006_C_04_LINEAR-BEARING | LINEAR-BEARING        | 4           |
| ***Fixings*** |                                     |             |
| LEC_006_F_01_M4-8MM-SOCKETHEAD-SCREW LEC_006_F_06_M4-8MM-SOCKETHEAD-SCREW  | 4          |
| LEC_006_F_02_M4-16MM-BUTTONHEAD-SCREW | M3-16MM-BUTTONHEAD-SCREW | 4 |
| LEC_006_F_03_M4-SLIDE-NUT | M5_SLIDE-NUT            | 4          |
| LEC_006_F_04_M3-HEX-NUT | M3_HEX-NUT            | 4          |
| LEC_006_F_05_M3-16MM-BUTTONHEAD-SCREW | M3-16MM-BUTTONHEAD-SCREW| 4  |
| LEC_006_F_06_CABLE-TIE-3MM | CABLE-TIE-3MM         | 12           |

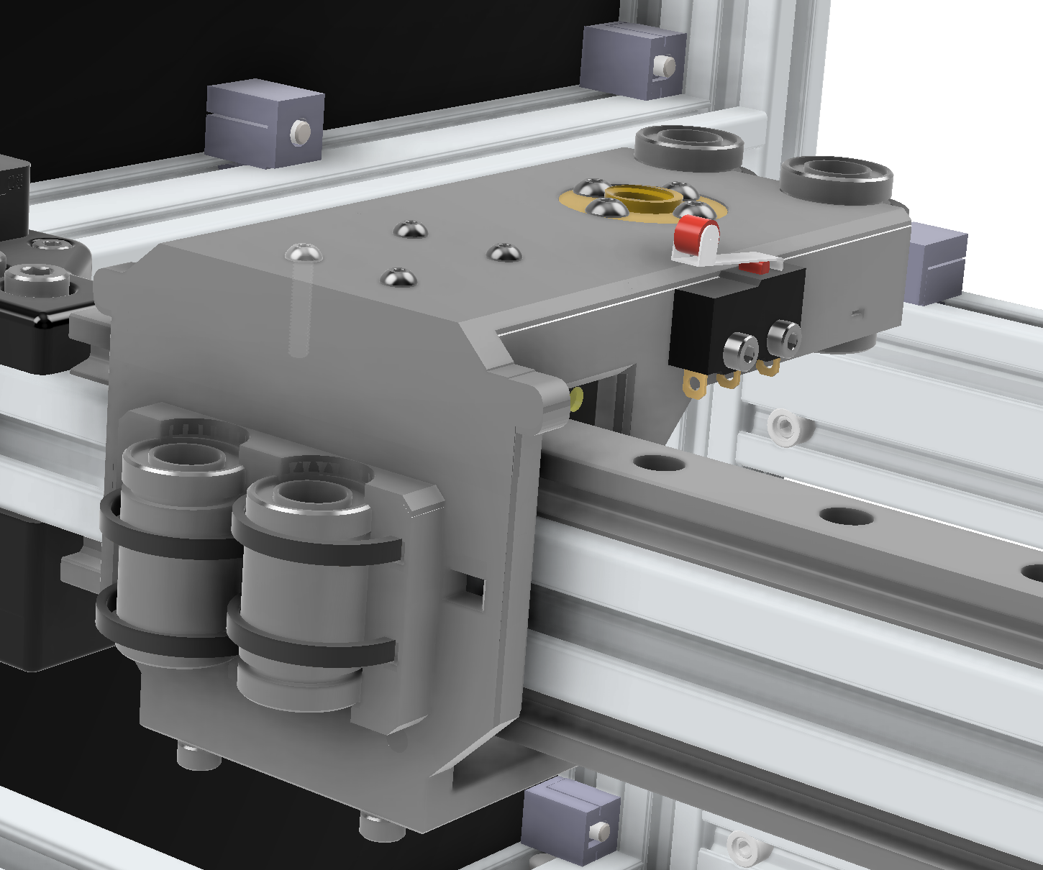
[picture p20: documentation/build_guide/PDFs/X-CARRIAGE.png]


**FIGURE 7.0**

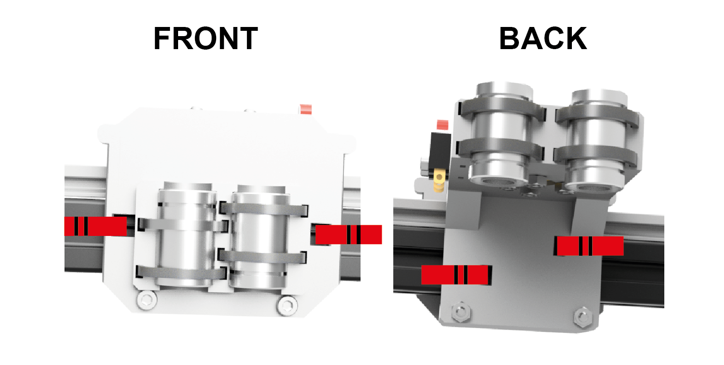
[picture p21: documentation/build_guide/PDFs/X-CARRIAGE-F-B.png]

**FIGURE 7.1**

**7.1** The X-carriage is used to mount the Z-carriage. Start by taking the **Z-AXIS-RAIL-UPPER** and **Z-AXIS-RAIL-LOWER** and sliding on the **Z-AXIS-RAIL-CARRIAGE-LOWER** and **Z-AXIS-RAIL-CARRIAGE-UPPER**. Insert **M3_10mm_SUNKENHEAD-SCREW** into the rails and loosely screw on **M3_SLIDE-NUT** to the threads of these. Attach each of the assembled rails to the **2020-318mm-RAIL** and screw this in place. 

**7.2** Next, attach the **2020-318mm-RAIL** to the Y-carriage. Start by slotting the rails into the lower M5 slide nuts from the Y-carriage assembled in stage 16, and screw these in place. Next, turn the entire frame upside down, this will help with the following steps. Take the complimentary upper sections of each side of the Y-carriage assembled in step **18**, and screw these in place, by screwing in the 35mm M3 screws containing the washers and bearings, and M5 screws with attached slide nuts. The X and Y axis should now move freely. 

**7.3** To construct the Z-axis carriage, start by screwing the **LEADSCREW-NUT** into the **Z-AXIS-CARRIAGE-UPPER** using **M3_16mm_BUTTONHEAD-SCREW** and **M3_HEX-NUT**. Next, take each of the **LINEAR-BEARING**, and fix these in place using **CABLE-TIE-5mm**. Make sure that the thread hole of the cable tie is on the outer side of the carriage. Leave this to one side for now, as we need to attach the belts before attaching this to the rail carriages. 

-----------------
### 8.0 X-Y AXIS BELTS
-----------------

***Toothed belts are responsible for creating movement in the X and Y directions, from the movement of the shafters of the X and Y stepper motor shafts. The routing of the belts is important. So too is ensuring that the belts are attached to the x-carriage by looping back around on themselves teeth to teeth, to prevent slipping.***

| **Parts** | **Shorthand Name**                    |**QUANTITY**|
|-----------|----------------------------------------|-------------|
| **Printed** |                                      |             |
| LEC_007_P_01_TOP-CORNER_L | TOP-CORNER_L           | 1           |
| LEC_007_P_02_TOP-CORNER_R | TOP-CORNER_R           | 1           |
| LEC_007_P_03_Z-AXIS-CARRIAGE-LOWER | Z-AXIS-CARRIAGE-LOWER | 1   |
| **Components** |                                    |             |
| LEC_007_C_GT2-BELT | GT2-BELT                       | 2 |
| **Fixings** |                                       |             |
| LEC_007_F_01_M2.5-10MM_BUTTONHEAD-SCREW | M2.5-10MM-BUTTONHEAD-SCREW  | 4 |
| LEC_007_F_03_M2.5-12MM_BUTTONHEAD-SCREW | M2.5-12MM-BUTTONHEAD-SCREW   | 4 |
| LEC_007_F_06_M3-18MM-BUTTONHEAD-SCREW | M3_18MM-BUTTONHEAD-SCREW | 4 |
| LEC_007_F_01_M3-35MM-SOCKETHEAD-SCREW | M3_35MM-SOCKETHEAD-SCREW | 6 |
| LEC_007_F_02_M5-10MM-SOCKETHEAD-SCREW | M5_10MM-SOCKETHEAD-SCREW | 2 |
| LEC_007_F_03_M5-SLIDE-NUT | M5_SLIDE-NUT            | 6           |
| LEC_007_F_04_CABLE-TIE-5MM | CABLE-TIE-5MM          | 8           |

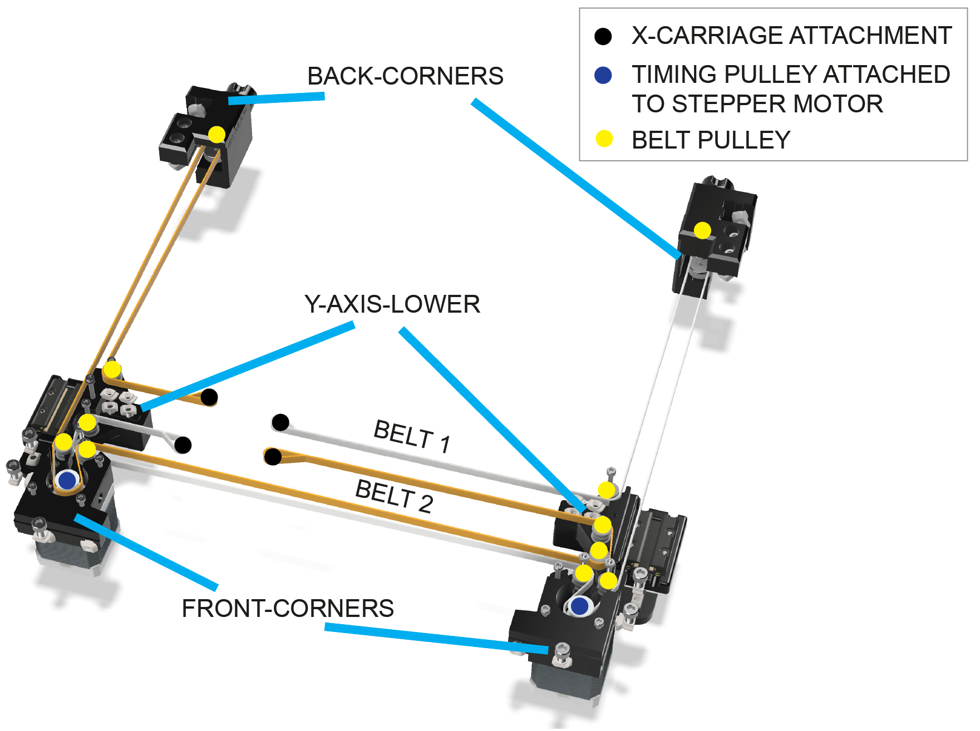
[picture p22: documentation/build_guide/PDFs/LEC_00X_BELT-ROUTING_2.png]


***FIGURE 8.0. Belt routing with top front corner parts removed for clarity, and belts coloured to aid clarity. Belts attach to the x-carriage*** 

***NOTE: Each belt, loops through the belt tensioners at the back of the instrument. Once the belt has followed the path, loop around the carriage in the same way as for the other end. At this stage, make sure that the belt tensioner is inserted into the rear of the instrument, and the tensioner knob is screwed on loosely. This is important, to ensure sufficient belt before cutting. Pull the belt tight with a pair of pliers along its route and then secure with a cable tie. Now you can cut the belt.***

**8.1** You should start with two **GT2-BELTS**. Take one end, and pass it through the hole on the Z-carriage constructed in step **23**, and loop it back on itself. The teeth of the **GT2-BELT** should lock into eachother. Secure this in place using two **CABLE-TIE-5mm**. Do the same with the second belt on the opposite end of the carriage. Route the belts through the front corner, Y carriage and back corners as per the diagram, and secure each belt to the back of the z-carriage using the same method described earlier in this step. When routing the belts through the Y-carriage, you may need to use a pair of tweezers to pull the belt through. 

**8.2** Now the belts have been routed and attached to the Z-axis carriage, attach the Z-axis carriage to the upper rail carriage on the upper X rail using **M2.5_12mm_BUTTONHEAD-SCREW**. Screw the **Z-AXIS-CARRIAGE-LOWER**  to the lower rail carriage using **M2.5_10mm_BUTTONHEAD-SCREW**. The **Z-AXIS-CARRIAGE-LOWER** is also screwed to the Z-carriage constructed in step **23** using **M3_18mm_BUTTONHEAD-SCREW**. 

**8.3**ADD STEP TO ATTACH THE FRONT CORNERS. LEFT HAND SIDE NEEDS SMALLER M3 SCREWS TO ATTACH STEPPER MOTORS, 35MM CURRENTLY TOO LONG. IDEALLY NEED 30MM. 

**8.4** Once the belts and Z-carriage are in place, tighten the belts using the back corner knobs constructed in step **10**. 

***The belt should then be tightened, by using the tensioner knobs at the back of the instrument, pulling the belts backwards. They should be sufficiently tight so as not to be sagging, but not 'guitar string' tight.***

-----------------
### 9.0 Z-AXIS
-----------------

***The z-carriage carries the optics - including the camera, lens and light, and enables movement up and down. The carriage is mounted on the x-carriage and slides up and down on rods, driven by a leadscrew attached to the z-axis stepper motor***

| **Parts** | **Shorthand Name**                    |**QUANTITY**|
|-----------|----------------------------------------|-------------|
| ***Printed*** |                                    |             |
| LEC_008_P_01_Z-CARRIAGE | Z-CARRIAGE               | 1           |
| LEC_008_P_02_LIGHT-BRACKET-TOP | LIGHT-BRACKET-TOP | 1           |
| LEC_008_P_03_LIGHT-BRACKET-BOTTOM | LIGHT-BRACKET-BOTTOM | 1     |
| LEC_008_P_04_OPTICS-MOUNT | OPTICS-MOUNT           | 1           |
| LEC_008_P_05_CAM-MOUNT | CAM-MOUNT                 | 1           |
| LEC_008_P_06_RAIL-INSERT | RAIL-INSERT             | 1           |
| LEC_008_P_07_OPTIC-SCREW | OPTIC-SCREW             | 1           |
| LEC_008_P_08_ZLIM-TRIGGER | ZLIM-TRIGGER           | 1           |
| LEC_008_P_09_BACK-ROD-SECURE | BACK-ROD-SECURE     | 2          |
| LEC_008_P_10_FRONT-ROD-SECURE | FRONT-ROD-SECURE   | 2          |
| LEC_008_P_11_LIGHT-MOUNT | LIGHT-MOUNT             | 1           |
| LEC_008_P_12_LIGHT-KNOB | LIGHT-KNOB               | 1           |
| LEC_008_P_13_LIGHT-DIFFUSER | LIGHT-DIFFUSER       | 1           |
| LEC_008_P_14_LIGHT-SLIDER | LIGHT-SLIDER       | 1           |
| ***Components*** |                                 |             |
| LEC_008_C_01_Z-STEPPER | Z-STEPPER                 | 1           |
| LEC_008_C_02_CAM | CAM                             | 1           |
| LEC_008_C_03_CAM-HDMI | CAM-HDMI                             | 1      |
| LEC_008_C_04_LENS | LENS                           | 1           |
| LEC_008_C_05_KFL08 | KFL08-BEARING                 | 1           |
| LEC_008_C_06_FLEX-COUPLING | FLEX-COUPLING         | 1           |
| LEC_008_C_07_Z-SCREW | Z-SCREW                     | 1           |
| LEC_008_C_08_F-ROD | F-ROD                         | 2           |
| LEC_008_C_09_R-ROD | R-ROD                         | 2           |
| LEC_008_C_10_LED-RING | LED-RING                   | 1           |
| LEC_008_C_11_Z-LEADSCREW | LEADSCREW                   | 1           |
| ***Fixings*** |                                    |             |
| LEC_008_F_01_M2.5-10MM-SOCKETHEAD-SCREW | M2.5-10MM-SOCKETHEAD-SCREW   | 4 |
| LEC_008_F_02_M3-10MM-SOCKETHEAD-SCREW | M3-10MM-SOCKETHEAD-SCREW       | 3 |
| LEC_008_F_03_M3-12MM-SOCKETHEAD-SCREW | M3-12MM-SOCKETHEAD-SCREW | 11|
| LEC_008_F_04_M3-HEX-NUT | M3-HEX-NUT               | 8           |
| LEC_008_F_05_M5-10MM-SOCKETHEAD-SCREW | M5-10MM-SOCKETHEAD-SCREW | 2 |
| LEC_008_F_06_M5-HEX-NUT | M5-HEX-NUT               | 2           |
| LEC_008_F_06_M2.5-12MM | M2.5-12MM-SOCK-SCREW               | 2     |



**FIGURE 9.0. Z-axis assembly** 

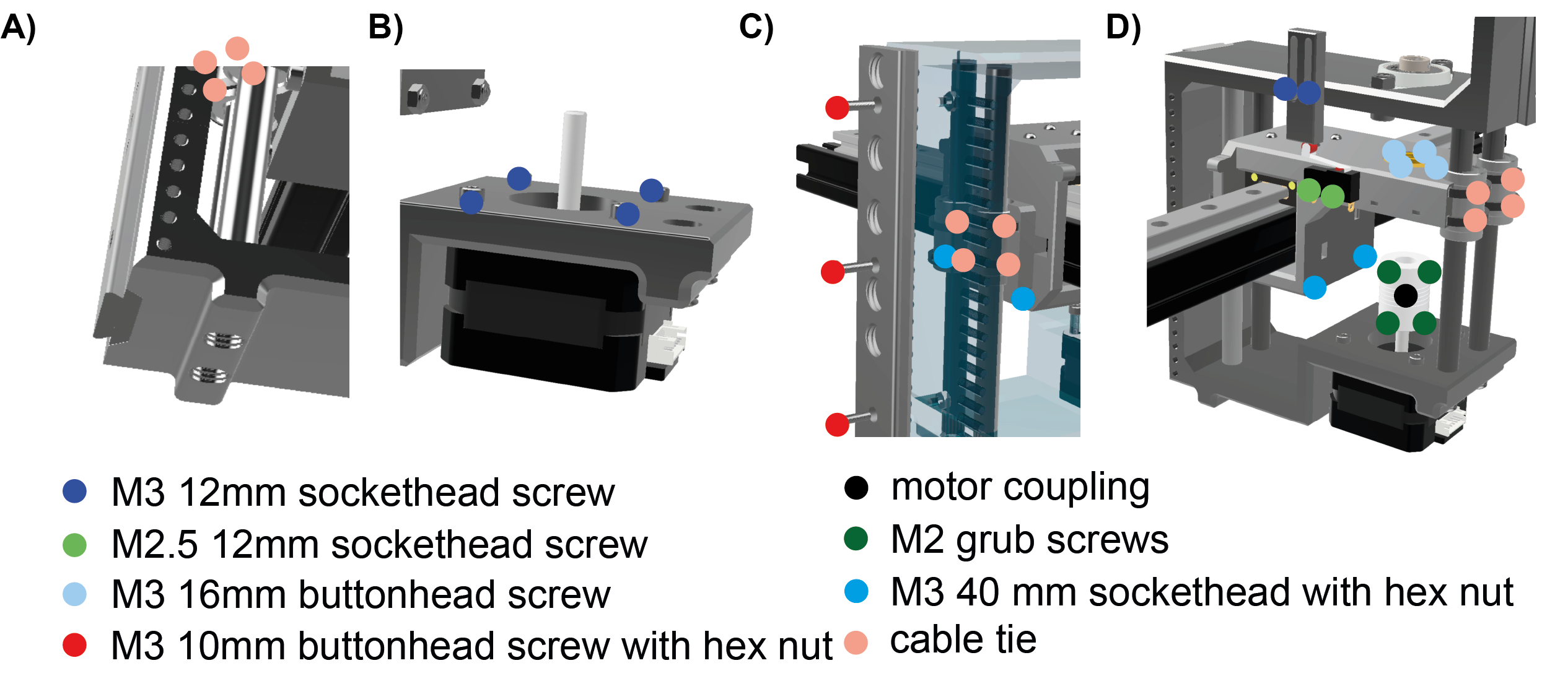
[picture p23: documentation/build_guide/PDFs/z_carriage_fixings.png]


**FIGURE 9.1 Z-axis assembly 2**

**9.1** Start by attaching various printed parts and components to the **Z-CARRIAGE**. Start by screwing the **RAIL-INSERT** to the **Z-CARRIAGE** using **M3_12mm_SOCKETHEAD-SCREW**. Next, attach the **ZLIM-TRIGGER** using **M3_12mm_SOCKETHEAD-SCREW**, attach the **KFL08** using **M5_10mm_SOCKETHEAD-SCREW** and **M5_HEX-NUT**, and attach the **Z-STEPPER** using **M3_12mm_SOCKETHEAD-SCREW**. Finally, attach the **FLEX-COUPLING** to the drive shaft of the **Z-STEPPER**, which should be secured using ..

**9.2**. Next, we need to attach the **Z-CARRIAGE** to the Z-carriage on the X-rail. To do this, orient the **Z-CARRIAGE** as per the diagram, and pass the two **F-ROD** (longer rods) through the holes on the front underside of the **Z-CARRIAGE**. The rods need to pass through the linear bearings attached to the Z-carriage on the Z-rail, before slotting into the grooves on the underside of the top face of the **Z-CARRIAGE**. Gently tap these into place, and screw in the **FRONT-ROD-SECURE** to secure these rods in place. Do the same for the **R-ROD** (shorter rods) and secure these using **BACK-ROD-SECURE**. Finally, pass the **Z-SCREW** through the **KFL08** and screw it into the **FLEX-COUPLING**. Secure this in place by screwing the **Z-SCREW** into the **KFL08**. Gently turning the **FLEX-COUPLING** should now move the **Z-CARRIAGE** up and down. 

**9.3** Next, attach the **OPTICS-MOUNT** and **LIGHT-MOUNT** by slotting them into the front and of the **Z-CARRIAGE** respectively. Screw the **OPTIC-SCREW** into the **CAM-MOUNT**, and screw the **CAM-MOUNT** into the **CAM-MOUNT** using **M2.5_10mm_SOCKETHEAD-SCREW**. 

**9.4** Finally, assemble the bracket for the light ring. Attach the **LIGHT-BRACKET-TOP** to the **LIGHT-BRACKET-BOTTOM** using **M3_10mm_SOCKETHEAD-SCREW** and **M3_HEX-NUT**. Leave this assembly to one side for now, as we need to solder and wire up the light ring before attaching it to the **LIGHT-MOUNT**. 

-----------------
### 10.0 ELECTRONICS
-----------------

***The electronics of the LabEmbryoCam are concentrated in the electronics enclosure mounted on the rear of the instrument. A number of wiring looms and individual cables, connect this to different parts of the instrument, via labelled ports on the electronics enclosure***

| **PARTS** | **SHORTHAND NAME**                       |**QUANTITY**|
| ----------|------------------------------------------|-------------|
| ***3D PRINTED*** |                                      |             |
| LEC_009_P_01_MOUNTING-PLATE | MOUNTING-PLATE         | 1           |
| LEC_009_P_02_PORT-PLATE | PORT-PLATE         | 1           |
| LEC_009_P_03_FAN-PLATE | FAN-PLATE         | 1           |
| LEC_009_P_04_FRONT-BREAKOUT-MOUNT | FRONT-BOARD-MOUNT        | 1      |
| LEC_009_P_05_CABLE-MOUNT | CABLE-MOUNT         | 8          |
| LEC_009_P_06_R-FRONT-PANEL | R-FRONT-PANEL         | 1          |
| LEC_009_P_07_L-FRONT-PANEL | L-FRONT-PANEL         | 1          |
| LEC_009_P_08_ELEC-MOUNT-BOTTOM | BOTTOM-ENCLOSURE-BRACKET | 1   |
| LEC_009_P_09_ELEC-MOUNT-TOP | TOP-ENCLOSURE-BRACKET| 1          |
| LEC_009_P_10_MICROCONTROLLER-BRACKET | MICROCONTROLLER-BRACKET| 1     |
| LEC_009_P_11_DISPLAY-FASCIA | DISPLAY-FASCIA| 1          |
| LEC_009_P_12_DISPLAY-REAR | DISPLAY-REAR| 1          |
| LEC_009_P_13_DISPLAY-ARM | DISPLAY-ARM| 1          |
| LEC_009_P_14_DISPLAY-BRACKET | DISPLAY-BRACKET| 1          |
| LEC_009_P_15_CABLE-BRACKET | CABLE-BRACKET| 10          |
| LEC_009_P_16_Y-LIM-SWITCH-MOUNT | Y-LIM-SWITCH-MOUNT| 1          |
| ***COMPONENTS*** |                                  |             |
| LEC_009_C_01_THOR-ELEC-ENC | ELECTRONICS-ENCLOSURE | 1       |
| LEC_009_C_02_THOR_ELEC-ENC-BASEPLATE | ELECTRONICS-BASE-PLATE| 1    |
| LEC_009_C_03_RPI4 | RPI4                             | 1            |
| LEC_009_C_04_USB-HUB | USB-HUB                       | 1            |
| LEC_009_C_05_PSU-SEASONIC300SUG | PSU-SEASONIC300SUG | 1            |
| LEC_009_C_06_DUET | DUET                             | 1            |
| LEC_009_C_07_ARDUINO | ARDUINO                       | 1            |
| LEC_009_C_08_RJ45-CONN | RJ45-CONN                   | 1            |
| LEC_009_C_09_SWITCH | SWITCH                         | 1            |
| LEC_009_C_10_HDMI-CONN | HDMI-CONN                   | 2            |
| LEC_009_C_11_USB-CONN | USB-CONN                     | 3           |
| LEC_009_C_12_DB15-M-CONN | DB15-M-CONN               | 1            |
| LEC_009_C_13_DB25-M-CONN | DB25-M-CONN               | 1            |
| LEC_009_C_14_ATX-BREAKOUT | ATX-BREAKOUT             | 1            |
| LEC_009_C_15_CASE-FAN | CASE-FAN                       | 1            |
| LEC_009_C_16_RPI_FAN | RPI_FAN                       | 1    |
| LEC_009_C_17_CSI-HDMI-CAM-HAT | CAM-HAT                | 1            |
| LEC_009_C_18_RPI-HQ-CAM | CAM                | 1            |
| LEC_009_C_19_LENS | LENS                | 1            |
| LEC_009_C_20_HDMI-F-F-COUPLER | HDMI-COUPLER         | 1            |
| LEC_009_C_21_USB-C-R-ANGLE-CABLE | USB-C-R-ANG         | 2            |
| LEC_009_C_22_MICRO-HDMI-R-ANGLE-CABLE | U-HDMI-CABLE  | 1            |
| LEC_009_C_23_USD-CARD | USD-CARD  | 1            |
| LEC_009_C_24_USBA-ARDUINO | ARD-USB  | 1            |
| LEC_009_C_25_USBMIC-DUET | DUET-USB  | 1            |
| LEC_009_C_26_DISPLAY-HDMI | DISP-HDMI  | 1            |
| LEC_009_C_27_DISPLAY-USB | DISP-USB  | 1            |
| LEC_009_C_28_DISPLAY | DISPLAY  | 1            |
| LEC_009_C_28_JOYSTICK | JOYSTICK  | 1            |
| LEC_009_C_28_Z-BUTTONS | Z-BUTTONS  | 2            |
| ***FIXINGS*** |      |      |
| LEC_009_F_01_M3_12mm_COUNTERSUNK-SCREW | M3_12mm_COUNTERSUNK-SCREW | 3 
| LEC_009_F_02_M3_DB-JACK-SCREW-HEAD | JACK-SCREW | 4    |
| LEC_009_F_03_M3_NYLOC-NUT | NYLOC-SCREW | 4    |
| LEC_009_F_04_M3_USB-SCREWS | NYLOC-SCREW | 1    |
| LEC_009_F_05_TRIPOD-SCREW | CAM-SCREW | 1    |
| LEC_009_F_06_M4-HEX-40MM-SCREW | DISPLAY-HEX-SCREW | 2    |
| LEC_009_F_07_M4-NYLOC-HEX-NUT | DISPLAY-HEX-NUT | 2    |
| LEC_009_F_08_M2.5-8MM-SOCKETHEAD-SCREW | DISPLAY-M2.5-SOCKETHEAD | 4  |
| LEC_009_F_09_M5-6MM-BUTTONHEAD-SCREW | DISPLAY-M5-BUTTONHEAD | 4    |
| LEC_009_F_10_M3-8MM-SOCKETHEAD-SCREW | DISPLAY-M3-SOCKETHEAD | 4    |
| LEC_009_F_11_M5-6MM-BUTTONHEAD-SCREW | CABLE-BRACKET-M5-BUTTONHEAD |10| | LEC_009_F_12_M5-SLIDENUT | M5-SLIDENUT | 14   |
| ***ELECTRONICS ASSEMBLIES*** |      |      |
| LEC_009_A_01_ELEC-ENC | ELECTRONICS-ENCLOSURE | 1    |
| LEC_009_A_02_25PIN-M-ELEC-ENC | 25PIN-ENC | 1    |
| LEC_009_A_03_25PIN-F-EXT | 25PIN-EXT | 1    |
| LEC_009_A_04_15PIN-M-ELEC-ENC | 15PIN-ENC | 1    |
| LEC_009_A_05_15PIN-F-EXT | 15PIN-EXT | 1    |
| LEC_009_A_06_FRONT-BOARD-ASSEMBLY | FRONT-BOARD | 1    |
| LEC_009_A_07_Z-BOARD-ASSEMBLY | Z-BOARD | 1    |

### 10.1 Overview
The LabEmbryoCam build requires six wiring looms, which are treated here as 'assemblies'. 
1. 25 pin wiring loom
    a) Inside the electronics enclosure (25PIN-EXT, 11.X)
    b) From the electronics enclosure to the front panel (25PIN-ELEC-ENC, 11.X)
    c) Front circuitboard assembly (FRONT-BOARD 11.X)
2. 15 pin wiring loom 
    a) Inside the electronics enclosure (15PIN-EXT, 11.X)
    b) From the electronics enclosure to the front panel (15PIN-ELEC-ENC, 11.X)
    c) Z-axis circuitboard assembly (Z-BOARD, 11.X)

For most builders, these will have been provided as already built 'assemblies', and can simply be attached to the relevant parts of the instrument. Nonetheless, for the assembly to be complete, the full details of how to create these wiring assemblies are provided at the end of the electronics section of the build guide, in the sections given for each part above.

-------------------
### 10.2 Electronics Enclosure
-----------------

***Electronics are mounted inside a metal enclosure, with 3D printed endplates. This enclosure is mounted
on the rear of the LabEmbryoCam, and connections made to the various components via cables and wiring
looms.***

Before fitting components to the electronics enclosure it is necessary to remove the existing metal fascias,
and replace with 3D printed fascias.

**10.2.1 Attaching fan end plate**

Replace each of the metal end fascias with one of each of the LEC_008_P_08_PORT-PLATE and
LEC_008_P_07_FAN-PLATE, using M3 COUNTERSUNK on the sides, and M3 NYLOC NUTS, and M3
COUNTERSUNK 12 MM underneath.

**WHICH WAY AROUND - PIC/GUIDE**

Fit Notura fan to FAN END PLATE (label facing plate, wire of fan in bottom corner) using 12 MM M3
BUTTONHEAD SCREWS and M3 NYLOC NUTs.

After fitting the fan, attach the end plate to the enclosure.using M3 6MM countersunk screws on the sides,
and M3 12MM countersunk screws and nyloc screws on the bottom.

**10.2.2. Assembling and attaching port end plate**

Attach ports and cables to the port end plate using screws included with the cables, or M2.5 12 MM
sockethead screws.
1. 3 x USB 3.0 ports
2. 2 x HDMI ports
3. 1 x Ethernet port
4. 1 x ON/OFF switch
DB15 and DB25 male ports should be attached to the port plate using D-SUB SCREW LOCKs and M3 NYLOC
NUTs.
5. 1 x DB25 port
6. 1 x DB15 port

----
### 10.3 Attaching Internal Components
------

## Electronics Enclosure (LEC_009_A_01)



**FIGURE 10.1** Electronics enclosure assembly

**10.3.3 Mounting electronics plate**
1. Attach the 3D printed plastic LEC_008_P_01_MOUNTING-PLATE to the threads of the electronics
enclosure (ensure 4 threaded inserts attached - 2 for PSU and 2 for microcontroller bracket). Using 3 x
M3 10 MM sockethead mm screws, and 1 x M3 10 MM COUNTERSUNK SCREW. NOTE that countersunk
screw is for the countersunk hole.
ADD FIG

**10.3.4 Mounting power supply**

1. Attach PSU bracket to the PSU using the included philips countersunk screws.. (IMG).
2. The mains socket connection of the PSU should fit tightly in the the PORT plate of the electronics
enclosure. Once fitted snuggly, attach the PSU to the electronics plate using two M XX MM
SOCKETHEAD SCREWS. Attach the PSU to the PORT plate using two XX MM buttonhead screws.
3. The power supply cable bundle must be modified to remove the unnecessary connectors (i.e. those
that don't fit directly to the ATX breakout). These cables should be cut and isolated with individual
heatshrink around each cable, and larger heatsink around the unneeded bundle of cables.

**10.3.5 Mounting microcontroller stack**

Important that the microcontroller stack is fitted in the following order.
1. Connect wires to header board and mount on microcontroller
1. 4 wires from DB15 - A2, A3, GND, 5V
2. 2 wires from 5V, GND -> ATX board 5V, GND
2. Attach printed mount to electronics board
3. Attach microcontroller to printed mount (with nyloc M2.5 nuts and ...)
ADD FIG

**10.3.6 Mounting Raspberry Pi stack**

1. Attach NVMe board to RPi - ensuring that the NVMe has first been flashed with the current LEC
opearting image.
2. Insert 3D printed spacers between RPI and NVMe board and use M2.5 16 MM screws - attach this stack
to the mounting points on the electronics board.
3. Attach ribbon cable to RPi connector
4. Mount arducam-csi adapter to the header pins
5. Feed ribbon cable through, ensuring it is facing relevant direction, to attach to the ribbon connector on
the Arducam-CSI board. Connect the 'Camera HDMI cable' from the port fascia connector.
6. Connect:
1. 90 degree USB cable from ATX board
2. USB port from USB-HUB to USB 3.0 (blue)
3. USB from SSD port to USB 3.0
4. 90 degree micro-HDMI -> Display
5. Ethernet from NETWORK PORT
ADD FIG

**10.3.7 ATX Breakout board**

1. Requires:
1. 2 x 200 mm wires (red and black) for 12V/GND -> 12V/GND on the Duet board
2. 1 x USB-C bare-end 5V/GND -> RPi
3. 2 x 250 mm (red, black) from microcontroller -> 5V / GND microcontroller
4. 2 x 200 mm wires (red, black) - PWR/CONN -> ON/OFF SWITCH
5. 2 x 350 mm barrel connector USB HUB -> 5V / GND
2. Mount ATX board to the electronics plate.
3. Double check that the screw underneath the ATX board (securing the electronics plate, is not making
contact with the undereside of the ATX board).

**10.3.7 USB Hub**

1. Connect barrel connector from ATX-BOARD to the barrel power connector on USB HUB.
2. Connect 90 degree USB-C from USB-HUB to a USB 3.0 port.
3. Connect peripherals to USB-A ports
| Port Destination Cable type                 |
|---------------------------------------------|
| USB 1 Arduino UNO USB B -> USB-A            |
| USB 2 Duet USB A -> Micro-USB               |
| USB 3 Peripheral USB Port USB PORT -> USB-A |
| USB 4 Display USB PORT -> USB-A             |

**10.3.8 Duet board**

1. Attach power from the ATX board wires.
2. Connect micro-USB from Duet board to USB-HUB
3. Connect limit switches from DB15 and DB25 connectors to the appropriate Duet 3 pin limit switch
connectors.
4. Connect stepper motors from DB15 and DB25 connectors from the appropriate Duet 3 stepper driver
connectors.
5. Ensure Duet microSD is flashed with current software from LEC Github repository.
DOUBLE-CHECK CONNECTORS
ADD FIG

---------------
### 10.4 Wiring Loom
---------------



**FIGURE 10.2 ** Wiring loom

Two wiring looms connect the majority of the electronic components in the LabEmbryoCam to the electronics enclosure on the rear of the instrument.

Begin by cutting the wires detailed below to the necessary lengths, for each of the looms. Each wire must be terminated with the appropriate conncetion types, and labelled acording to the guide below.

### 10.5 **Wiring Loom 1 - DB25**

***Runs from front of instrument and terminates to a DB25 female connector, that connects to the receptive male port on the electronics enclosure***

| WIRES REQUIRED     |         |             |
| ------------------ |         |  ---------- |
| **Wire type**      |**Function**         |  **Length** |
| 4 Multicore ribbon | X_Stepper_Motor |  100cm      |
| *BLACK* |  |      |
| *BLUE* |  |       |
| *GREEN* |  |        |
| *RED* |  |        |
| 4 Multicore ribbon | Y_Stepper_Motor | 65cm      |
| *BLACK* |  |      |
| *BLUE* |  |       |
| *GREEN* |  |        |
| *RED* |  |        |
| 2 Multicore ribbon | Y_Limit_Switch |  50cm     |
| *BLUE* |  |      |
| *YELLOW* |  |       |
| 2 Multicore ribbon | X_Limit_Switch |  50cm   |
| *BLUE* |  |      |
| *YELLOW* |  |       |

### 10.6 **Front Panel Wiring Hub**

-- change z-but colours

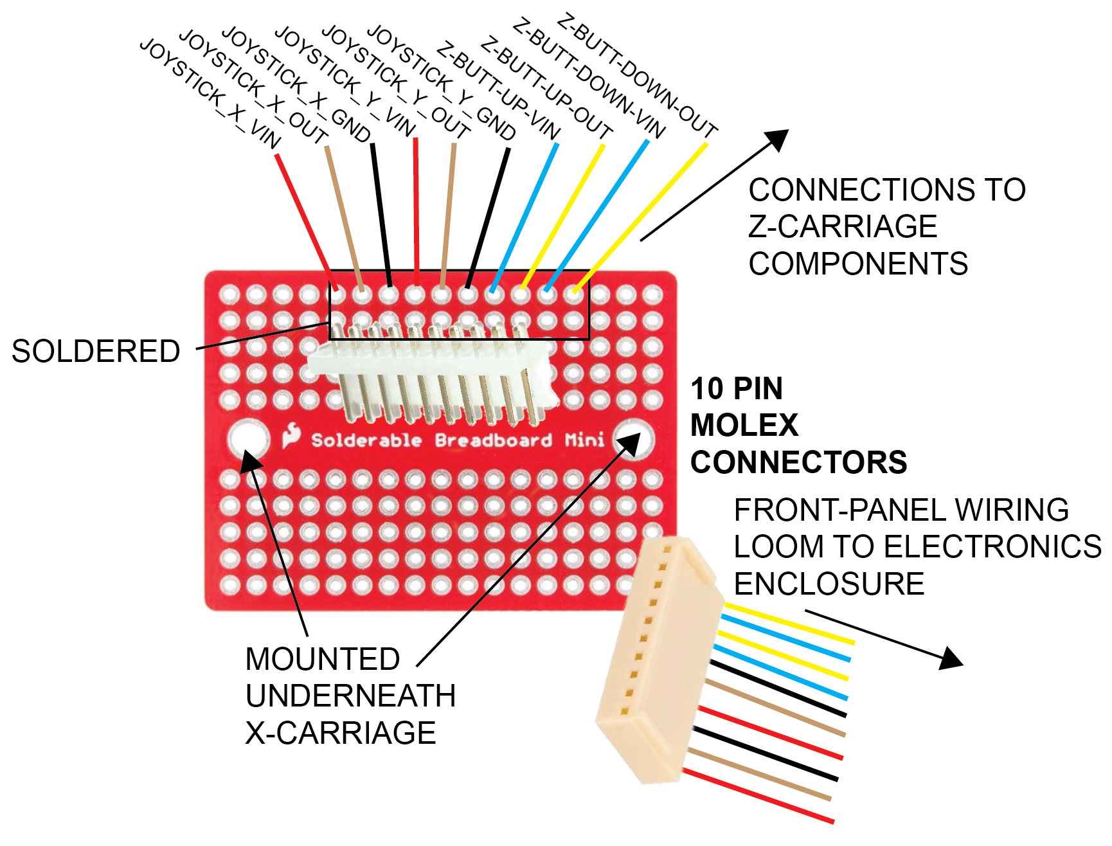
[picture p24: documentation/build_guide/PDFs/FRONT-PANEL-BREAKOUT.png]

**FIGURE 10.3**


***FIGURE 10.4** FRONT PANEL BREAKOUT ...

-----------
#### 10.7 **Wiring Loom 2 - DB15**
-----------

***Runs from Z-carriage to a DB15 female connector, that connects to the receptive male port on the electronics enclosure***

| WIRES REQUIRED     |                 |            |
| ------------------ | --------------- | ---------- |
| **Wire type**      | **Function**    | **Length** |
| 4 Multicore ribbon | Z_Stepper_Motor | 85cm       |
| 2 Multicore ribbon | Z_Limit_Switch  | 50cm       |
| 4 Multicore ribbon | LED             | 50cm       |

| WIRES REQUIRED                             |              |            |                   |
| ------------------------------------------ | ------------ | ---------- | ----------------- |
| **Wire type**                              | **Function** | **Length** | **Termination A** |
| 4 Multicore ribbon                         | LED          | 50cm       | BARE              |
| 2 Multicore ribbon                         | Z-limit      |            | 25cm              |
| ** double check these z-carriage lengths** |              |            |                   |

Black, Blue, Green, Red

**diagram/lengths needed**

-----------
### 10.8 **Z Wiring Hub**
-----------

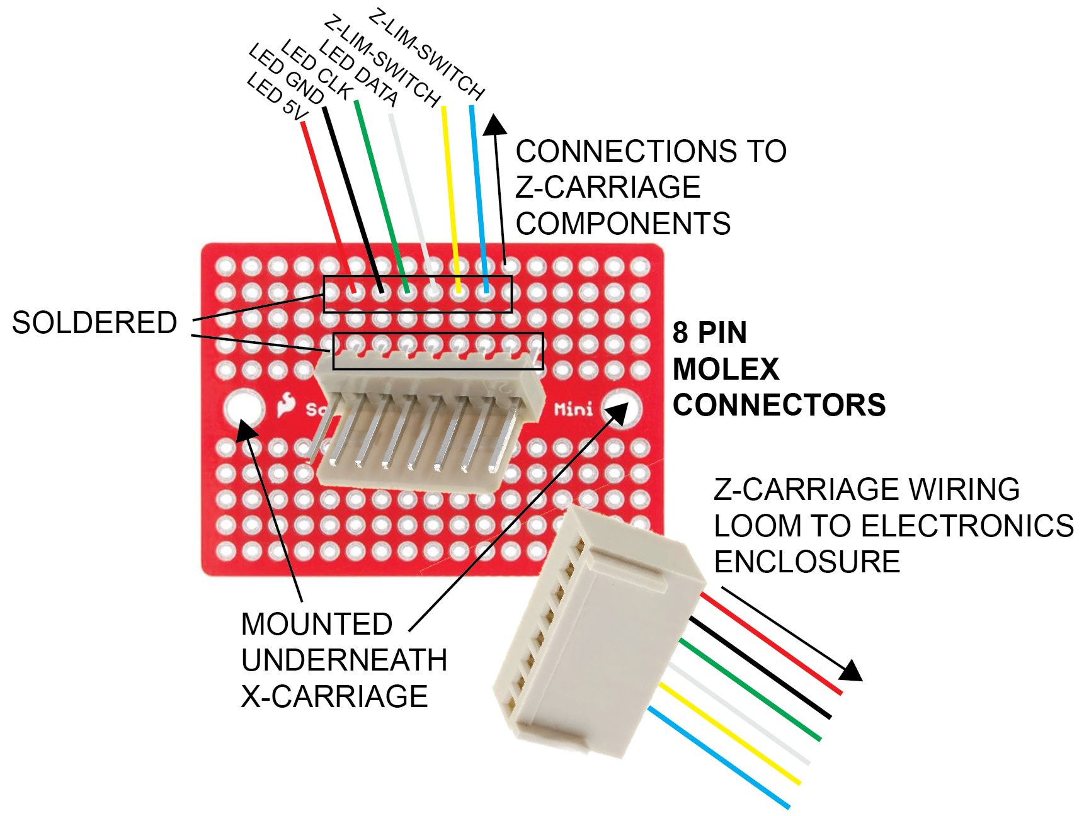
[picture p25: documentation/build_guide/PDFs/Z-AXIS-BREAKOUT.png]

***FIGURE 10.5**. Z-AXIS-BREAKOUT

**diagram/lengths needed**

-----------
### 10.9 Electronics Enclosure Wiring
---------------

| WIRES REQUIRED       |Function  |Length |Termination	|Routing|
| -------------------- | ---- |---| --- | ---|
|***DB25*** | | | | |
| 4 Multicore ribbon   | X Stepper motor| 20cm |Wire -> MOLEX|DB25->DUET|
| 4 Multicore ribbon   | Y Stepper motor|  20cm |Wire -> MOLEX|DB25->DUET|
| 1 x Blue, 1 x Yellow | X Limit switch|  25cm |Wire -> MOLEX|DB25->DUET|
| 1 x Blue, 1 x Yellow | Y Limit switch|  25cm |Wire -> MOLEX|DB25->DUET|
| 4 Multicore ribbon   | Z buttons|  20cm |Wire -> Wire| DB25->ARDUINO|
| 3 Multicore ribbon   | X Joystick|  20cm  |Wire -> Wire|DB25->ARDUINO|
| 3 Multicore ribbon   | Y Joystick|  20cm  |Wire -> Wire|DB25->ARDUINO|
|***DB15*** | | | | |
| 1 x Blue, 1 x Yellow | Z Limit switch|  25cm |Wire -> MOLEX|DB15->DUET|
| 4 Multicore ribbon   | Z Stepper motor|  20cm |Wire -> MOLEX|DB15->DUET|
| 4 Multicore ribbon   | LED | 20cm |Wire -> MOLEX|DB15->ARDUINO|
| **Integrated Cables**       |   |      |        |          |
| HDMI   | Camera signal|  XX  |HDMI->HDMI|UPPER_HDMI_PORT->PI-CSI_BOARD|
| HDMI   | Control panel|  XX  |HDMI->HDMI|LOWER_HDMI_PORT->RPI4 MICROHDMI|
| USB   | Solid State Drive|  XX  |USB->USB|USB PORT->RPI-USB3|
| USB   | Accessory|  XX  |USB->USB|USB PORT->USB-HUB|
| ETHERNET   | Networking|  XX  |RJ45->RJ45|RJ45-PORT->RPI4-RJ45|

-----------------
## 12.0 VIBRATION-INSULATION
-----------------

The bottom corners should be attached to the instrument towards the end of the build, to prevent damage during the build process. 

Each corner encompasses two vibration insulation components - a sorbothene foot, and a 3D printed leafspring. Once assembled, care should be taken not to apply too much pressure onto the instrument.

| **Parts**                             | **Shorthand Name**       | **QUANTITY** |
| ------------------------------------- | ------------------------ | ------------ |
| ***Printed***                         |                          |              |
| LEC_002_P_01_FR/BL-BOTTOM-CORNER      | FR/BL_BOTTOM-CORNER      | 2            |
| LEC_002_P_01_FR/BR-BOTTOM-CORNER      | FR/BR_BOTTOM-CORNER      | 2            |
| LEC_002_P_03_LEAFSPRING               | LEAFSPRING               | 4            |
| ***Components***                      |                          |              |
| LEC_002_C_01_SORBOTHENE-FEET          | SORBOTHENE-FEET          | 4            |
| ***Fixings***                         |                          |              |
| LEC_002_F_01_M5_10MM-BUTTONHEAD-SCREW | M5_10MM-BUTTONHEAD-SCREW | 12           |
| LEC_002_F_02_M5-SLIDE-NUT             | M5_SLIDE-NUT             | 12           |
| LEC_002_F_03_M6-12MM_BUTTONHEAD-SCREW | M6_12MM-BUTTONHEAD-SCREW | 4            |
| LEC_002_F_04_M6-45MM_BUTTONHEAD-SCREW | M6_45MM-BUTTONHEAD-SCREW | 4            |
| LEC_002_F_05_M6-HEX-NUT               | M6_HEX-NUT               | 4            |

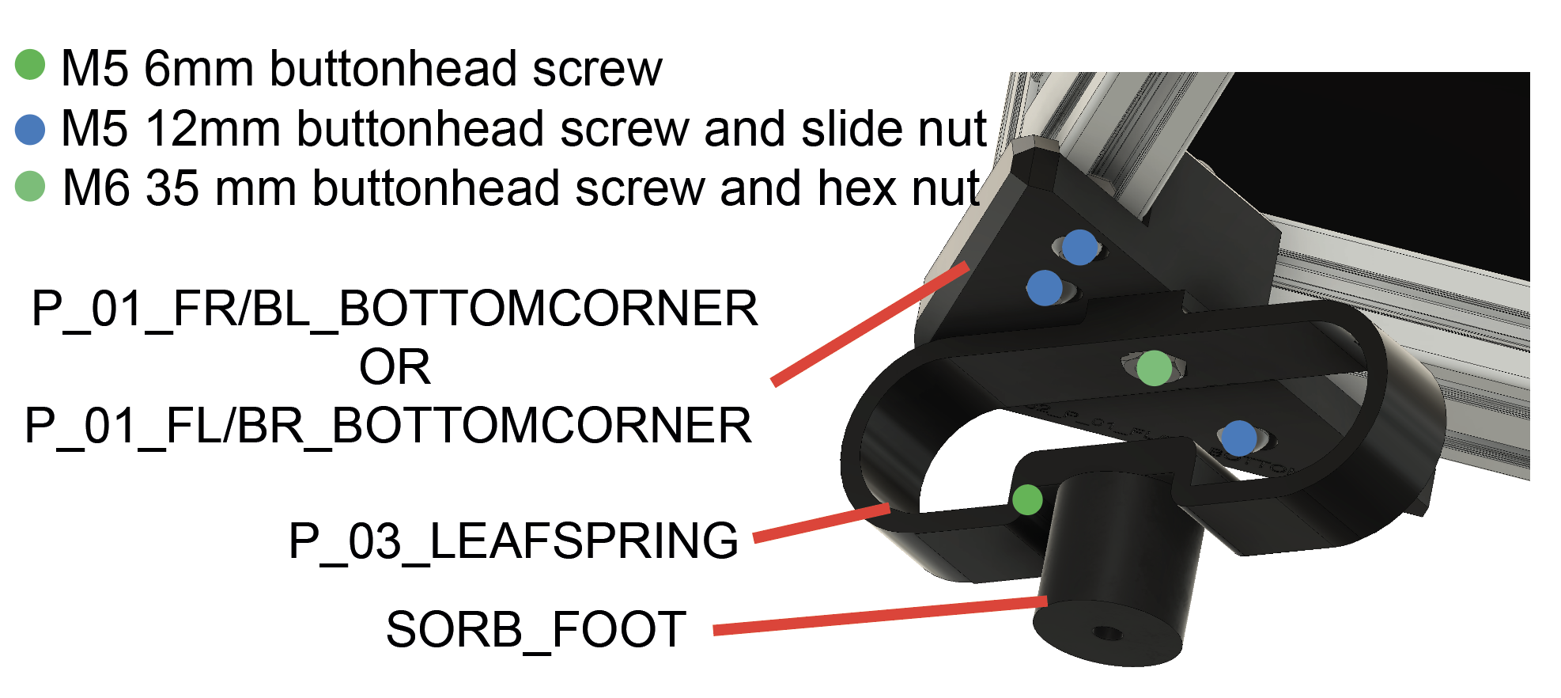
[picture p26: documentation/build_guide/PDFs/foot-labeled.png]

**FIGURE 12.0**

**12.1** The bottom corners are attached to the base of the frame and are required to attach components used to insulate against vibrations, that may cause interference with acquired video footage. Start by attaching the 2 **FR/BL_BOTTOM-CORNER** and 2 **FR/BR_BOTTOM_CORNER** pieces to the underside corners of the assembled frame, using **M5_10mm_BUTTONHEAD-SCREWS** and **M5_SLIDE-NUTS**. 

**12.2** Next, construct the vibration insulating feet to each of the bottom corners. Start by screwing the **SORBOTHENE-FEET** to the **LEAFSPRING** using **M6_12mm_BUTTONHEAD-SCREWS**. Then place **M6_HEX-NUTS** into the grooves within each **LEAFSPRING**. Screw in each of the assembled feet into the bottom corner pieces, using the **M6_HEX-NUTS** and **M6_45mm_BUTTONHEAD-SCREWS**. 

-----------------

### Panel attachment

-----------------

While not essential, attaching plastic panels to the LabEmbryoCam is encouraged as for little cost, they help to keep the instrument clean, protect moving parts and cables and they keep it looking tidy. Note the size of the panels required in the bill of materials and their 
locations above. Before installing the panels, insert M3 square nuts into the holes at the top and bottom of each spacer. The square nuts should slide as far as they can be pushed, using a small allen key or similar, so that the hole in the nut aligns with the hole in the 3D printed spacer.

-----------------
### DISPLAY INSTALLATION
-----------------
| **Parts**                             | **Shorthand Name**       | **QUANTITY** |
| ------------------------------------- | ------------------------ | ------------ |
| ***Printed***                         |                          |              |
| LEC_002_P_XX      | XX      | 2            |
| LEC_002_P_XX     | XX      | 2            |
| LEC_002_P_03_LEAFSPRING               | LEAFSPRING               | 4            |

--------------
### 13.0 LID
------------------

***While not essential, the lid keeps the instrument clean and offers some protection from interference during an experiment***. 

| **PARTS** | **SHORTHAND NAME**                       |**QUANTITY**|
| ----------|------------------------------------------|-------------|
| ***COMPONENTS*** |                                      |             |
| LEC_010_C_01_HINGE | HINGE         | 2           |
| LEC_010_C_02_TOP-LID-PLASTIC-311X315 | TOP-LID-PLASTIC         | 1    |
| LEC_010_C_03_FRONT-LID-PLASTIC-315X59 | FRONT-LID-PLASTIC        | 1  |
| LEC_010_C_04_HANDLE | HANDLE        | 1  |
| LEC_010_C_05_CUBE-CONNECTORS | CUBE-CONNECTORS        | 6  |
| ***EXTRUSION*** |                                      |             |
| LEC_010_E_01_2020-312MM | 2020-312MM         | 2           |
| LEC_010_E_02_2020-303MM | 2020-303MM         | 3           |
| LEC_010_E_02_2020-60MM | 2020-60MM         | 2           |
| ***FIXINGS*** |                                      |             || |LEC_010_F_01_M5-SLIDENUT | M5-SLIDENUT        | 2  |
|LEC_010_F_01_M5-8MM-SOCKETHEAD-SCREW | M5-8MM-SOCKETHEAD-SCREW      |2|

--------------
## 14.0 TESTING
------------------

***This section is still a work in progress - with testing procedures.***

--------------
### 14.1 Duet Board Testing
------------------
The Duet XYZ board has a control interface not routinely used in the operation of the LEC, but useful during initial setup.

To access it, connect the board directly to a network connection via the ethernet port on the board itself (not the ethernet). Turn on the LEC, and navigate to the Terminal and type ``` cutecom```. 

This will open a window allowing us to determine the IP address of the Duet board on the network. Once open - choose the Device ```/dev/tty/ACMX```, with X usually being either 0, 1 or 2 from the dropdown.

Click 'Open'. If joystick or light is returned, this means you have selected the wrong Device - so try another.

Type ```M115``` and if all is working, you should see the current firmware version.

If so, type ```M552 S0```, followed by ```M552 S1``` to deactivate, and then reactivate the network connection.

You should see 'Network running. IP address = XXX.XXX.X.XXX', with the XXX corresponding to the address of your own instrument on your network.

You can now access the Duet board of the LabEmbryoCam on your network via this IP address, from any other device connected to the same network. You will be prompted for a password. The default password for LabEmbryoCams is ```radix```

To check the input power to the Duet board, use M122 in CuteCom.

--------------
## 14.0 TROUBLESHOOTING
------------------
### Vibrating and/or noisy stepper motor - but no movement
This is typically caused by a bad connection to the stepper motor caused by either a damaged cable, or incorrect wiring. If the instrument was previously working then incorrect wiring is unlikely. Consider a wholesale replacement of the DB-25 wiring loom. Before doing so, by opening the electronics enclosure you can directly connect the stepper motor to the Duet board to see if this resolves the issue  - if so, you can be assured that wiring is indeed the issue.

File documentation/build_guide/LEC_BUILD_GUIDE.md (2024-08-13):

# LabEmbryoCam Build Guide

**An opensource platform for automated measurement of developing animals**

***The LabEmbryoCam is a project originating with the EmbryoPhenomics research group at the University of Plymouth, UK. It has been made possible by support from UKRI, NERC, BBSRC and Plymouth Science Park***.

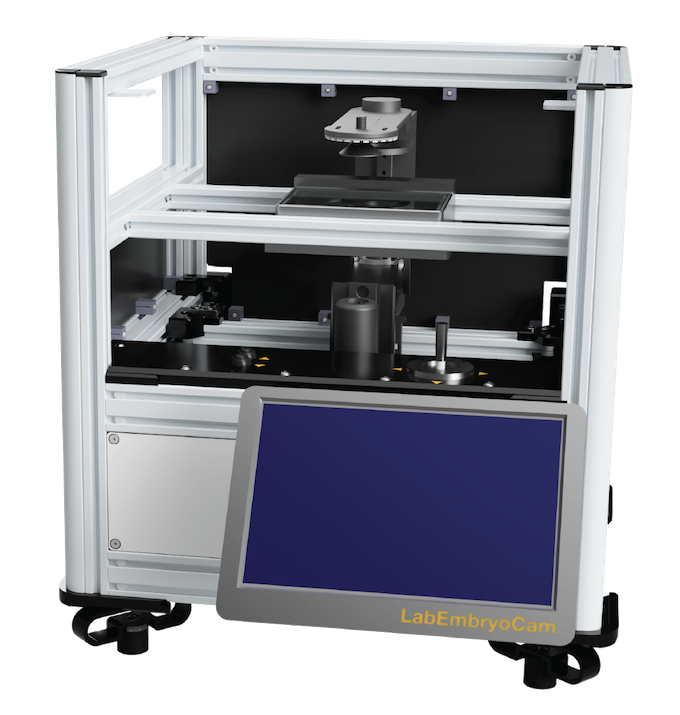
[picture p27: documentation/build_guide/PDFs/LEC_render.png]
Frame
 

-----------------
### 1.0 BACKGROUND
-----------------

The LabEmbryoCam provides:

* Automated movement of a camera and lighting in the X, Y and Z direction, over prolonged periods making it well suited to recording the process of embryonic development in aquatic animals.
* A custom user interface for easy setup of experiments, within a multiwell plate format, but also has sufficient flexibility for other culture formats - petri dishes, or even custom culture solutions.
* Incorporates an optional humifidification chamber to significantly reduce evaportation thereby solving one of the key challenges of long term timelapse imaging of aquatic animals.
* Vibration dampening addressing vibration, the enemy of timelapse imaging. 
* LabEmbryoCam incorporates sorbothene feet, 3D printed leafsprings and cable dampeners to minimise its effects on your imaging.
* A low cost, modular and versatile phenotyping platform taking advantage of 3D printed parts, single board computers, microcontrollers, stepper motors and lower cost cameras and lenses.
* Hackability this is an active project - if in doubt about any aspect of this instrument and its suitability to your activities, just ask.

**The LabEmbryoCam consists of both hardware and software, and the process of building both is described in the following series of pages.**

**Required Materials**

Building a LabEmbryoCam requires a range of mechnical and electrical parts, and 3D printed parts. 

* [**Components Required**](bom.md)

* [**Fixings required**](BOM_fixings.md)

The LabEmbryoCam is built using commonly available and low-cost consumer electronics, mechanical parts and 3D printed parts. Links and prices are provided as a guide, but prices vary and there is also significant scope for changing components, or suppliers due to availability, price, or user requirements.

A significant assortment of screws, nuts and washers are required to build a LabEmbryoCam (Bill of materials for fixings in **Required Materials**. To simplify the process of sourcing these parts, a kit of the required fixings can be bought here: https://www.modelfixings.co.uk/embryophenomics.htm (note this kit is not completely up-to-date)

To reduce the number of orders required to source these parts, parts are grouped to a few key suppliers and these are indicated in the bill of materials. Most parts are, however, available from a range of suppliers. There is considerable scope for changing parts to suit your use case.

A CAD model of the LabEmbryoCam is accessible here: https://a360.co/3ZnY7k5

## 1.1 Assembly Structure

The LabEmbryoCam project is organised as a range of different parts, and the numbering of parts indicates which assembly the part belongs to.

| **ASSEMBLY** | **DESCRIPTION**         |
| ---------- | ----------------------- |
| LEC_001    | Rexroth Aluminium Frame |
| LEC_002    | Bottom Corners          |
| LEC_003    | Back Corners            |
| LEC_004    | Front Corners           |
| LEC_005    | Y Carriage              |
| LEC_006    | X Carriage              |
| LEC_007    | Z Carriage              |
| LEC_008    | Electronics             |

## 1.2 Build Sequence

1. Frame
2. Back corners
3. Front corners
4. Y-carriage
5. X-carriage
6. Belts/Front top
7. Z-carriage
8. Bottom corners
9. Electronics
10. Panels

----------------

## 1.3 3D Printed Parts

STLs are the 3D model files, provided for producing the 3D printed parts. There are > 70 3D printed parts, with many requiring multiple copies. The (n) in the name of some parts indicates the number of that part that needs printing. For each section in this build guide, the required parts are listed. See the build guide for further information on 3D printing these parts.

Unless otherwise stated in **Specific Print Settings** parts should be printed using PETG with a minimum of 30 % infill, with 6 perimeters, 6 bottom layers and 6 top layers.

| **Parts**   |**Quantity**|**Specific Print Settings**|
|--------------------------------|------|-----|
| LEC_002_P_01_FR/BL_BOTTOM-CORNER   | 2           ||
| LEC_002_P_01_FR/BR_BOTTOM-CORNER   | 2           ||
| LEC_002_P_03_LEAFSPRING            | 4           ||
| LEC_003_P_01_BACK-CORNER_L         | 1           ||
| LEC_003_P_02_BACK-CORNER_R         | 1           ||
| LEC_003_P_03_PULLEY_L              | 1           ||
| LEC_003_P_04_PULLEY_R              | 1           ||
| LEC_003_P_05_KNOB                  | 2           ||
| LEC_004_P_01_BOTTOM-CORNER_L       | 1           ||
| LEC_004_P_02_BOTTOM-CORNER_R       | 1           ||
| LEC_004_P_03_LOW-CORNER-BRACKET_L  | 1           ||
| LEC_005_P_01_YAXIS-LOWER_L         | 1           ||
| LEC_005_P_02_YAXIS-LOWER_R         | 1           ||
| LEC_005_P_03_YAXIS-UPPER_L         | 1           ||
| LEC_005_P_04_YAXIS-UPPER_R         | 1           ||
| LEC_005_P_05_YAXIS-LIMSWITCH_MOUNT | 1           ||
| LEC_006_P_01_Z-AXIS-CARRIAGE-UPPER | 1           ||
| LEC_007_P_01_TOP-CORNER_L          | 1           ||
| LEC_007_P_02_TOP-CORNER_R          | 1           ||
| LEC_006_P_02_Z-AXIS-CARRIAGE-LOWER | 1           ||
| LEC_008_P_01_Z-CARRIAGE            | 1           |CF-PETG|
| LEC_008_P_02_LIGHT-BRACKET-TOP     | 1           ||
| LEC_008_P_03_LIGHT-BRACKET-BOTTOM  | 1           ||
| LEC_008_P_04_OPTICS-MOUNT          | 1           ||
| LEC_008_P_05_CAM-MOUNT             | 1           ||
| LEC_008_P_06_RAIL-INSERT           | 1           ||
| LEC_008_P_07_OPTIC-SCREW           | 1           ||
| LEC_008_P_08_ZLIM-TRIGGER          | 1           ||
| LEC_008_P_09_BACK-ROD-SECURE       | 2           ||
| LEC_008_P_10_FRONT-ROD-SECURE      | 2           ||
| LEC_008_P_11_LIGHT-MOUNT           | 1           ||
| LEC_008_P_12_LIGHT-KNOB            | 1           ||
| LEC_008_P_13_LIGHT-DIFFUSER        | 1           ||
| LEC_009_P_01_MOUNTING-PLATE        | 1           ||

## 1.4 Fixings

The LabEmbryoCam is assembled using a number of fixings. These are listed in the table below, but in the build guide itself, they are split between the assembly sections.

| **Parts**                                         |**Quantity**|
|---------------------------------------------------|-------------|
| **M2.5**                                          |             |
| M2.5_10mm_SOCKETHEAD-SCREW                        | 6           |
| M2.5_10mm_BUTTONHEAD-SCREW                        | 4           |
| M2.5_12mm_BUTTONHEAD-SCREW                        | 4           |
| **M3**                                            |             | 
| M3_10mm_SOCKETHEAD-SCREW                          | 3           |
| M3_10mm_SUNKENHEAD-SCREW                          | 40          |
| M3_12mm_SOCKETHEAD-SCREW                          | 19          |
| M3_15mm_SOCKETHEAD-SCREW                          | 6           |
| M3_16mm_BUTTONHEAD-SCREW                          | 4           |
| M3_16mm_SOCKETHEAD-SCREW                          | 2           |
| M3_18mm_BUTTONHEAD-SCREW                          | 4           |
| M3_35mm_SOCKETHEAD-SCREW                          | 16          |
| M3_50mm SOCKETHEAD-SCREW                          | 2           |
| M3_HEX-NUT                                        | 20          |
| M3_SLIDE-NUT                                      | 40          |
| M3_WASHER                                         | 30          |
| **M4**                                            |             |
| M4_40mm_HEX-BOLT                                  | 2           |
| M4_HEX-NUT                                        | 2           |
| **M5**                                            |             |
| M5_10mm_BUTTONHEAD-SCREW                          | 20          |
| M5_10mm_SOCKETHEAD-SCREW                          | 9           |
| M5_14mm_SOCKETHEAD-SCREW                          | 2           | 
| M5_16mm_SOCKETHEAD-SCREW                          | 1           |
| M5_20mm_BUTTONHEAD-SCREW                          | 2           |
| M5_HEX-NUT                                        | 2           |
| M5_SLIDE-NUT                                      | 42          |
| **M6**                                            |             |
| M6_12mm_BUTTONHEAD-SCREW                          | 4           |
| M6_45mm_BUTTONHEAD-SCREW                          | 4           |
| M6_HEX-NUT                                        | 4           |
| **Other**                                         |             |
| FAST-CONNECTOR-SCREW                              | 56          |
| FAST-CONNECTOR-SLIDE-PIN                          | 56          |
| END-RAIL-COVER                                    | 4           |
| END-RAIL-COVER-ROUNDED                            | 4           |
| PANEL-FIXINGS                                     | 44          |
| CABLE-TIE-3mm                                     | 4           |
| CABLE-TIE-5mm                                     | 8           |

## 1.5 Components

The LabEmbryoCam is built using an array of components - in most instances, these are readily available online and not custom. The two exceptions are i) the IGUS rails are cut to 250 mm length and this can have a short leadtime (one week typically), and ii) the electronics enclosure has custom machined panels for the ports, and PCB mountings. 

All required components are listed in the table below, and are organised by the different assemblies.

| **Parts**                                         |**Quantity**|
|---------------------------------------------------|-------------|
| LEC_002_C_01_SORBOTHENE-FEET                      | 4           |
| LEC_003_C_01_F623ZZ-BEARING                       | 4           |
| LEC_004_C_01_F623ZZ-BEARING                       | 8           | 
| LEC_004_C_02_XY-STEPPER                           | 2           |
| LEC_004_C_03_TIMING-PULLEY                        | 2           |
| LEC_005_C_01_YAXIS-CARRIAGE_L                     | 1           |
| LEC_005_C_02_YAXIS-CARRIAGE_R                     | 1           |
| LEC_005_C_03_YAXIS-RAIL_L                         | 1           |
| LEC_005_C_04_YAXIS-RAIL_R                         | 1           |
| LEC_005_C_F623ZZ-BEARING                          | 8           |
| LEC_006_C_01_Z-AXIS-RAIL-UPPER                    | 1           |
| LEC_006_C_02_Z-AXIS-RAIL-LOWER                    | 1           |
| LEC_006_C_03_Z-AXIS-RAIL-CARRIAGE-LOWER           | 1           |
| LEC_006_C_04_Z-AXIS-RAIL-CARRIAGE-UPPER           | 1           |
| LEC_006_C_05_LEADSCREW-NUT                        | 1           |
| LEC_006_C_06_LINEAR-BEARING                       | 4           |
| LEC_006_C_07_LIM-SWITCH                           | 1           |
| LEC_007_C_GT2-BELT                                | 1           |
| LEC_008_C_01_Z-STEPPER                            | 1           |
| LEC_008_C_02_CAM                                  | 1           |
| LEC_008_C_03_LENS                                 | 1           |
| LEC_008_C_04_KFL08                                | 1           |
| LEC_008_C_05_FLEX-COUPLING                        | 1           |
| LEC_008_C_06_Z-SCREW                              | 1           |
| LEC_008_C_07_F-ROD                                | 2           |
| LEC_008_C_08_R-ROD                                | 2           |
| LEC_008_C_09_LED-RING                             | 1           |
| LEC_009_C_01_THOR-CUST-BASE-PLATE                 | 1           |
| LEC_009_C_02_THOR-CUST-PORT-PLATE                 | 1           |
| LEC_009_C_03_THOR-CUST-FAN-PLATE                  | 1           |
| LEC_009_C_04_THOR_EC2030BR                        | 1           |
| LEC_009_C_05_RPI4                                 | 1           |
| LEC_009_C_06_USB-HUB                              | 1           |
| LEC_009_C_07_PSU-SEASONIC300SUG                   | 1           |
| LEC_009_C_08_DUET                                 | 1           |
| LEC_009_C_09_ARDUINO                              | 1           |
| LEC_009_C_10_RJ45-CONN                            | 1           |
| LEC_009_C_11_SWITCH                               | 1           |
| LEC_009_C_12_HDMI-CONN                            | 2           |
| LEC_009_C_13_USB-CONN                             | 2           |
| LEC_009_C_14_DB15-M-CONN                          | 1           |
| LEC_009_C_15_DB25-M-CONN                          | 1           |
| LEC_009_C_16_ATX-BREAKOUT                         | 1           |
| LEC_009_C_17_FAN                                  | 1           |

## 1.6 CAD

The LabEmbryoCam is modelled using the CAD software Autodesk Fusion360 - freely availabile for hobbyist use, or with an educational license. 

***INTERACTIVE AND DOWNLOADABLE CAD MODEL***: https://a360.co/3ZnY7k5

--------

-----------------
### 2.0 ASSEMBLY
-----------------

-----------------
### 3.0 ALUMINIUM EXTRUSION FRAME
-----------------

***The LabEmbryoCam frame is constructed using aluminium extrusion of different cross-sections and lengths. Aluminium extrusion is aluminium of a shape that enable fixing parts to be connected, for connecting extrusion together, or for attaching parts to the extrusion. Here we use Bosch Rexroth extrusion and the accompanying fast connectors to build the frame.***

| **Parts** | **Shorthand Name **                   |**Quantity**|
|-----------|----------------------------------------|-------------|
| ***Extrusion*** |                                  |             |
| LEC_001_E_01_2040-EXTRUSION-356MM | 2040-356MM     | 8           |
| LEC_001_E_02_2040-EXTRUSION-336MM | 2040-336MM     | 2           |
| LEC_001_E_03_2020-EXTRUSION-418MM-ROUNDED | 2020-418MM-ROUNDED | 2 |
| LEC_001_E_04_2020-EXTRUSION-416MM | 2020-416MM     | 4           |
| LEC_001_E_05_2020-EXTRUSION-356MM | 2020-356MM     | 2           |
| ***Fixings*** |                                    |             |
| LEC_001_F_01_FAST-CONNECTOR-SCREW | FAST-CONNECTOR-SCREW | 56     |
| LEC_001_F_02_FAST-CONNECTOR-SLIDE-PIN | FAST-CONNECTOR-SLIDE-PIN |56|
| LEC_001_F_03_2020-END-COVER | 2020-END-COVER        | 4           |
| LEC_001_F_04_2020-ROUNDED-END-COVER | 2020-ROUNDED-END-COVER | 4  |
| LEC_001_F_05_PANEL-FIXINGS | PANEL-FIXINGS          | 44          |
| LEC_002_F_01_M5-10MM-BUTTONHEAD-SCREW | M5-10MM-BUTTONHEAD-SCREW | 12 |
| LEC_002_F_02_M5-SLIDE-NUT             | M5_SLIDE-NUT             | 12 |  | ***3D Printedd*** |                                    |             |
| LEC_002_P_01_FR/BL_BOTTOM-CORNER      | FR/BL_BOTTOM-CORNER      | 2  |
| LEC_002_P_01_FR/BR_BOTTOM-CORNER      | FR/BR_BOTTOM-CORNER      | 2  |



**FIGURE 3.0 Connecting lengths of aluminium extrusion together**. **Fast connector screw** (1 and 2), used to tighten into the **fast connector slide pin** (3). 

** ****

***In the guide we refer to 2020 extrusion, which is 20 mm x 20 mm in cross section, whereas 2040 extrusion is 20 mm x 40 mm in cross section. 2020 extrusion with a rounded corner is also used on each outer upright corner of the instrument.***. 



**FIGURE 3.2 Frame design**. 

**3.1** Start by constructing the rear of the frame (2 x **2040-336mm-RAIL**, 2 x **2020-416mm-RAIL**. Take each **2020-416mm-RAIL**, and into the inside groove slide in 4 **FAST-CONNECTOR-SLIDE-PIN** into each rail. Insert the **FAST-CONNECTOR-SCREW** into each **2040-336mm-RAIL**, move these in position following the diagram in Figure 2, and then tighten each screw using the 3mm allen key. 

**3.2**Then add the horizontal rails into this rear frame (8 x **2040-356mm-RAIL**, 2 x **2020-418mm-ROUNDED-RAIL**). Lie down the assembled rear frame on the back face and then insert 4 **FAST-CONNECTOR-SLIDE-PIN** into the upward facing grooves. Insert the **FAST-CONNECTOR-SCREW** into each **2040-356mm-RAIL**, and insert these rails into the **FAST-CONNECTOR-SLIDE-PIN**. Do not tighten the allen keys at this stage, otherwise you will be unable to carry out the following steps. Insert 2 **FAST-CONNECTOR-SLIDE-PIN** into each **2020-418mm-ROUNDED-RAIL**. Insert the **2020-418mm-ROUNDED-RAIL** inline with the rear **2020-416mm-RAIL**. The spacing of each of the horizontal **2040-356mm-RAIL** must be established to fit each of the side panels. Use each of the side panels to adjust the spacing of these rails. Once all of these are in place, tighten all screws using the 3mm allen key.

**3.3**Take each of the **2020-356mm-RAIL** and insert the **FAST-CONNECTOR-SCREW**. Then insert each of the **FAST-CONNECTOR-SLIDE-PIN** into the ends of the **2020-356mm-RAIL**. The **2020-356mm-RAIL** used to mount the humidification chamber must be inserted so that the fast connectors are facing horizontally, i.e. the screws used to tighten the fast connectors are facing forwards, not upwards. This means there is then space at the end of each of these rails to attach the humidification chamber. Make sure to orient the slide pins so that the grooves are in line with the **FAST-CONNECTOR-SCREW**. Slide the rails and the **FAST-CONNECTOR-SLIDE-PIN** into the 2nd from the top **2040-356mm-RAIL**. Do not tighten these screws as they will have to be aligned with the humidification chamber mounts later in the build. 

**3.4**Next, assemble the front of the frame. Take the remaining 2 x **2020-416mm-RAIL** and insert 2 **FAST-CONNECTOR-SLIDE-PIN** into the inward facing grooves on each rail. Inset the **FAST-CONNECTOR-SCREW** into the 2 remaining **2040-336mm-RAIL**,  and assemble these as per the diagram. Again, use the front panel to adjust the spacing between the top and bottom **2040-336mm-RAIL**. Insert **FAST-CONNECTOR-SCREW** and **FAST-CONNECTOR-SLIDE-PIN** into the ends of each of the horizontal **2040-356mm-RAIL**. Then slide in the assembled front rails into **FAST-CONNECTOR-SLIDE-PIN** in the horizontal **2040-356mm-RAIL**. Do no tighten the screws. Finally, slide into place the 2 remaining **2020-418mm-ROUNDED-RAIL** alongside the front frame. Once all are in place, tighten the **FAST-CONNECTOR-SCREW** using the 3mm allen key. 

**3.5** To finish, insert the plastic end rail covers (4 x **END-RAIL-COVER** and 4 x **END-RAIL-COVER-ROUNDED**). **PANEL-FIXINGS** can then be added to each of the railings. These are added on the underside and bottom of the **2040-356mm-RAIL** and **2040-336mm-RAIL**, and can be spaced out using the complementary panels. Do not fix the panels yet as they will get in the way of subsequent steps.

-----------------
### 4.0 BACK CORNERS
-----------------

***The back corners are central to effective routing of the belts that create X and Y movement of the instrument. The knobs at the rear of the back corner contribute to this functioning by allowing adjustment of the tension of each of the two belts in the instrument.***

| **Parts** | **Shorthand Name**                     |**QUANTITY**|
|-----------|----------------------------------------|-------------|
| ***Printed*** |                                    |             |
| LEC_003_P_01_BACK-CORNER_L | BACK-CORNER_L         | 1           |
| LEC_003_P_02_BACK-CORNER_R | BACK-CORNER_R         | 1           |
| LEC_003_P_03_PULLEY_L | PULLEY-L                  | 1           |
| LEC_003_P_04_PULLEY_R | PULLEY-R                  | 1           |
| LEC_003_P_05_KNOB | KNOB                           | 2           |
| ***Components*** |                                 |             |
| LEC_003_C_01_F623ZZ-BEARING | F623ZZ-BEARING       | 4           |
| ***Fixings*** |                                    |             |
| LEC_003_F_01_M3-16MM_SOCKETHEAD-SCREW | M3-16mm_SOCKETHEAD-SCREW | 2|
| LEC_003_F_02_M3-WASHER | M3-WASHER                | 6           |
| LEC_003_F_03_M4-40MM_HEX-BOLT | M4-40MM_HEX-BOLT  | 2           |
| LEC_003_F_04_M4-HEX-NUT | M4-HEX-NUT              | 2           |
| LEC_003_F_05_M5-10MM_BUTTONHEAD-SCREW | M5-10MM_BUTTONHEAD-SCREW | 8|
| LEC_003_F_06_M5-SLIDE-NUT | M5-SLIDE-NUT        | 8           |



**FIGURE 4.0 FIGURE**

**4.1** The back corners of the LECs are used to feed through the belts, and to adjust the tension of these. Start by constructing each of the rear tensioners, and the associated tensioner knobs. Into the **PULLEY_L** and **PULLEY_R**, screw in the **M4_40mm_HEX-BOLT** so that the thread is sticking out of the back. Next, screw in the **M3_16mm_SOCKETHEAD-SCREWS** into just the base of each and screw each of the components into the inside of the pulleys in this order: **M3_WASHER**, **F623ZZ-BEARING**, **M3_WASHER**, **F623ZZ-BEARING**, **M3_WASHER**. 

**4.2.** Next, we need to attach the **BACK-CORNER_L** and **BACK-CORNER_R**. Start by adding the **M5_SLIDE-NUTS** into the frame. For each side, add 2 **M5_SLIDE-NUTS** into the inside top groove of the **2040-356mm-RAIL** that is 2nd from the bottom, and 2 **M5_SLIDE-NUTS** to the back of the **2020-416mm-RAIL**. Then fix the **BACK_CORNER_L** and **BACK_CORNER_R** in place. Line up the **M5_SLIDE-NUTS** inline with the screw holes on each 3D printed part, and screw these place using the **M5_10mm_BUTTONHEAD-SCREWS**. 

**4.3** Finally, push each of the assembled pulleys into the groove of the **BACK-CORNER_L** and **BACK-CORNER_R** so that the thread of the **M4_40mm_HEX-BOLTS** is coming out of the back of the machine. Insert **M4_HEX-NUTS** into the groove at the rear of the **KNOB**, and then loosely screw on each of the knobs to the thread of the **M4_40mm_HEX-BOLTS**. 

-----------------
### 5.0 FRONT CORNERS
-----------------

***The front corners are complex parts that are crucial for effective functioning of the instrument. The belts must follow the outlined routes, and in the correct orientation, for the LEC to work as it should.***

| **Parts** | **Shorthand name**                    |**QUANTITY** |
|-----------|----------------------------------------|-------------|
| ***Printed*** |                                    |             |
| LEC_004_P_01_BOTTOM-FRONT-CORNER-LEFT | BOTTOM-CORNER-L     | 1|
| LEC_004_P_02_BOTTOM-FRONT-CORNER-RIGHT | BOTTOM-CORNER-R     |1|
| LEC_004_P_03_TOP-FRONT-CORNER-LEFT | TOP-CORNER-L | 1     |
| LEC_004_P_04_TOP-FRONT-CORNER-RIGHT | TOP-CORNER-R | 1     |
| LEC_004_P_05_BOTTOM-SMALL-LEFT-BRACKET | BOTTOM-SMALL-L | 1     |
| ***Components*** |                                 |             |
| LEC_004_C_01_F623ZZ-BEARING | F623ZZ-BEARING        | 12           |
| LEC_004_C_02_XY-STEPPER | XY-STEPPER                | 2           |
| LEC_004_C_03_TIMING-PULLEY | TIMING-PULLEY          | 2           |
| ***Fixings*** |                                     |             |
| LEC_004_F_01_M3-15MM-SOCKETHEAD-SCREW | M3-15MM-SOCKETHEAD-SCREW | 6|
| LEC_004_F_02_M3-35MM-SOCKETHEAD-SCREW | M3-35MM-SOCKETHEAD-SCREW | 6|
| LEC_004_F_03_M3-WASHER | M3-WASHER                  | 18          |
| LEC_004_F_04_M3-HEX-NUT | M3-HEX-NUT                   | 6           |
| LEC_004_F_05_M5-10MM-SOCKETHEAD-SCREW | M5-10MM-SOCKETHEAD-SCREW | 2|
| LEC_004_F_06_M5-20MM-BUTTONHEAD-SCREW | M5-20MM-BUTTONHEAD-SCREW | 2|
| LEC_004_F_07_M5-SLIDE-NUT | M5-SLIDE-NUT             | 8          |



**FIGURE 5.0. Front corners, with the **

**5.1.** The front corners are used to route the XY belts through the stepper motors. Start by adding the **BOTTOM-CORNER_L**, **BOTTOM-CORNER_R** and **LOW-CORNER-BRACKET_L** to the front corners of the frame. These are attached using **M5_10mm_SOCKETHEAD-SCREW**,  **M5_20mm_BUTTONHEAD-SCREW** and **M5_SLIDE-NUT**. To attach these, screw each of the screws in place, and loosely screw the slide nuts onto the thread of these. Push the entire piece into place in the frame and then tighten the screws using an allen key. 

**5.2.** Next, we need to assemble the bearings and stepper motors used to route the belts into the bottom front corner pieces. Start by attaching each of the **XY-STEPPER** to the bottom corner pieces. When viewed from the top, this will mean screwing a **M3_15mm_SOCKETHEAD-SCREW** into the top left and top right of the left and right bottom corner pieces, and **XY-STEPPER** screw holes respectively. Leave the **XY-STEPPER** attached by the single screw. 

**5.3.** Next, screw in 3 **M3_35mm_SOCKETHEAD-SCREW** into the underside of the **BOTTOM-CORNER_L** and **BOTTOM-CORNER_R**. Screw these in leaving approximately 12mm of thread facing vertically out of bottom corner pieces. Onto each of these threads, add these fixings in this order: **M3_WASHER**, **F623ZZ-BEARING**, **M3_WASHER**, **F623ZZ-BEARING**, **M3_WASHER**. Then, to the thread of the stepper motor, add the **TIMING-PULLEY**. The top of the timing pulleys should be at approximately the same height as the bottom corner pieces, and are screwed in place using an allen key. 

**5.4.** The top corner pieces are left out at this point, as we must assemble other components (**LEC_005_A_Y-CARRIAGE**, **LEC_006_A_X-CARRIAGE**, **LEC_007_A_BELTS**) first. 

-----------------
### 6.0 Y-AXIS
-----------------

***The y-carriage is responsible for front to back movement of the instrument. It relies on two linear rails mounted on either side of the instrument. Proper mounting of these two linear rails is important to prevent binding of the instrument during movements along the y-axis.***

| **Parts** | **Shorthand Name **                    |**QUANTITY**|
|-----------|----------------------------------------|-------------|
| ***Printed*** |                                    |             |
| LEC_005_P_01_YAXIS-LOWER | YAXIS-LOWER         | 2           |
| LEC_005_P_02_YAXIS-UPPER | YAXIS-UPPER         | 2           |
| LEC_005_P_03_YAXIS-LIMSWITCH-MOUNT | YAXIS-LIMSWITCH-MOUNT | 1   |
| LEC_005_P_04_YAXIS-LIM-TRIG | YAXIS-LIMIT-TRIGGER | 1   |
| ***Components*** |                                  |             |
| LEC_005_C_01_YAXIS-CARRIAGE-L | YAXIS-CARRIAGE-L    | 1           |
| LEC_005_C_02_YAXIS-CARRIAGE-R | YAXIS-CARRIAGE-R    | 1           |
| LEC_005_C_03_YAXIS-RAIL-L | YAXIS-RAIL-L            | 1           |
| LEC_005_C_04_YAXIS-RAIL-R | YAXIS-RAIL-R            | 1           |
| LEC_005_C_05_F623ZZ-BEARING | F623ZZ-BEARING           | 8           |
| ***Fixings*** |                                     |             |
| LEC_005_F_01_M3_10MM-SOCKETHEAD-SCREW | M3-10MM-SOCKETHEAD-SCREW| 20|
| LEC_005_F_02_M3_12MM-SOCKETHEAD-SCREW | M3-12MM-SOCKETHEAD-SCREW| 8 |
| LEC_005_F_03_M3_35MM-SOCKETHEAD-SCREW | M3-35MM-SOCKETHEAD-SCREW| 4 |
| LEC_005_F_04_M3_50MM-SOCKETHEAD-SCREW | M3-50MM-SOCKETHEAD-SCREW| 1 |
| LEC_005_F_04_M3_60MM-SOCKETHEAD-SCREW | M3-60MM-SOCKETHEAD-SCREW| 1 |
| LEC_005_F_05_M3_WASHER | M3_WASHER                  | 12          |
| LEC_005_F_06_M3_HEX-NUT | M3_HEX-NUT                | 2           |
| LEC_005_F_07_M3_SLIDE-NUT | M3_SLIDE-NUT            | 20          |
| LEC_005_F_08_M5_10MM-SOCKETHEAD-SCREW | M5-10MM-SOCKETHEAD-SCREW | 3 |
| LEC_005_F_09_M5_14MM-SOCKETHEAD-SCREW | M5-14MM-SOCKETHEAD-SCREW | 2 |
| LEC_005_F_10_M5_16MM-SOCKETHEAD-SCREW | M5-16MM-SOCKETHEAD-SCREW | 1 |
| LEC_005_F_11_M5_SLIDE-NUT | M5_SLIDE-NUT            | 8           |



**FIGURE 6.0**

**6.1**. Now, the Y-carriage components need to be added to the frame. Take both the **YAXIS-RAIL_L** and **YAXIS-RAIL_R** and slide on the **YAXIS-CARRIAGE_L** and **YAXIS-CARRIAGE_R** to the end of each of these. 

**6.2.** Attach the **YAXIS-LOWER_L** and **YAXIS-LOWER_R** to the **YAXIS-CARRIAGE_L** and **YAXIS-CARRIAGE_R** respectively, using **M3_12mm_SOCKETHEAD-SCREW**. Into both the **YAXIS-LOWER_L** and **YAXIS-LOWER_R**, screw in **M5_10mm_SOCKETHEAD-SCREW** and **M5_16mm_SOCKETHEAD-SCREW**, and loosely screw on **M5_SLIDE-NUT** to the ends of these. 

**6.3** To attach these to the frame, insert **10mm_COUNTERSUNK-SCREW** into each of the rails, and loosely screw on **M3_SLIDE-NUT** to the threads of these. Insert the assembled rails and slide nuts into the grooves on the underside of the horizontal rails inbetween the front and back corner 3D printed parts. Make sure to push these up against the front corner pieces, and then using an allen key screw these into place. Once attached, the assembled carriages should move freely along the rails. 

**6.4** Next, construct the complimentary upper sections to the carriages. Take the **YAXIS-LIMSWITCH_MOUNT** and screw it into the **YAXIS-UPPER_L** using **M5_14mm_SOCKETHEAD-SCREW**. Then loosely screw on **M5_SLIDE-NUT** to the threads of these. Next, partically screw in **M3_35mm_SOCKETHEAD-SCREW**, so that the threads of the outer two screws are protruding equidistant with the height of the **YAXIS-LOWER_L**, and so the central is not protruding at all. Onto the threads of the outside two **M3_35mm_SOCKETHEAD-SCREW**, add these fixings in this order: **M3_WASHER**, **F623ZZ-BEARING**, **M3_WASHER**, **F623ZZ-BEARING**, **M3_WASHER**. 

**6.5** For the **YAXIS-UPPER_R**, these steps are slightly different. Screw in **M3_10mm_COUNTERSUNK-SCREW**, and loosely screw on **M5_SLIDE-NUT** to the threads of these. Next, take the **YAXIS-LIMTRIG** and screw this partically into the **YAXIS-UPPER_R** using **M3_50mm SOCKETHEAD-SCREW**, so that the thread does not protrude from the opposite hole. Screw in two more **M3_35mm_SOCKETHEAD-SCREW** either side of this, and assembled the fixings as per step **18**.  

**6.6** You should be left with 2 main assembled complimentary upper parts from steps **18** and **19**. Leave these to one side for now, we will attach these once the X-carriage in the next section has been assembled. 

-----------------
### 7.0 X-AXIS
-----------------

*** The x-carriage is the point of attachment for each end of the two belts responsible for X and Y motion. It slides from side to side on the linear rail attached to the 2020 piece of extrusion that creates the y-carriage.***

| **Parts** | **Shorthand Name**                     |**QUANTITY**|
|-----------|----------------------------------------|-------------|
| ***Extrusion*** |                                  |             |
| LEC_006_E_01_2020-318MM | 2020-318MM     | 1           |
| ***Printed*** |                                    |             |
| LEC_006_P_01_X-AXIS-CARRIAGE | Z-AXIS-CARRIAGE | 1   |
| ***Components*** Z|                                |             |
| LEC_006_C_01_X-AXIS-WS-RAIL | X-AXIS-WS-RAIL  | 1           |
| LEC_006_C_02_X-AXIS-WS-CARRIAGE | X-AXIS-WS-CARRIAGE  | 1           |
| LEC_006_C_03_LEADSCREW-NUT | LEADSCREW-NUT          | 1           |
| LEC_006_C_04_LINEAR-BEARING | LINEAR-BEARING        | 4           |
| ***Fixings*** |                                     |             |
| LEC_006_F_01_M4-8MM-SOCKETHEAD-SCREW LEC_006_F_06_M4-8MM-SOCKETHEAD-SCREW  | 4          |
| LEC_006_F_02_M4-16MM-BUTTONHEAD-SCREW | M3-16MM-BUTTONHEAD-SCREW | 4 |
| LEC_006_F_03_M4-SLIDE-NUT | M5_SLIDE-NUT            | 4          |
| LEC_006_F_04_M3-HEX-NUT | M3_HEX-NUT            | 4          |
| LEC_006_F_05_M3-16MM-BUTTONHEAD-SCREW | M3-16MM-BUTTONHEAD-SCREW| 4  |
| LEC_006_F_06_CABLE-TIE-3MM | CABLE-TIE-3MM         | 12           |



**FIGURE 7.0**


**FIGURE 7.1**

**7.1** The X-carriage is used to mount the Z-carriage. Start by taking the **Z-AXIS-RAIL-UPPER** and **Z-AXIS-RAIL-LOWER** and sliding on the **Z-AXIS-RAIL-CARRIAGE-LOWER** and **Z-AXIS-RAIL-CARRIAGE-UPPER**. Insert **M3_10mm_SUNKENHEAD-SCREW** into the rails and loosely screw on **M3_SLIDE-NUT** to the threads of these. Attach each of the assembled rails to the **2020-318mm-RAIL** and screw this in place. 

**7.2** Next, attach the **2020-318mm-RAIL** to the Y-carriage. Start by slotting the rails into the lower M5 slide nuts from the Y-carriage assembled in stage 16, and screw these in place. Next, turn the entire frame upside down, this will help with the following steps. Take the complimentary upper sections of each side of the Y-carriage assembled in step **18**, and screw these in place, by screwing in the 35mm M3 screws containing the washers and bearings, and M5 screws with attached slide nuts. The X and Y axis should now move freely. 

**7.3** To construct the Z-axis carriage, start by screwing the **LEADSCREW-NUT** into the **Z-AXIS-CARRIAGE-UPPER** using **M3_16mm_BUTTONHEAD-SCREW** and **M3_HEX-NUT**. Next, take each of the **LINEAR-BEARING**, and fix these in place using **CABLE-TIE-5mm**. Make sure that the thread hole of the cable tie is on the outer side of the carriage. Leave this to one side for now, as we need to attach the belts before attaching this to the rail carriages. 

-----------------
### 8.0 X-Y AXIS BELTS
-----------------

***Toothed belts are responsible for creating movement in the X and Y directions, from the movement of the shafters of the X and Y stepper motor shafts. The routing of the belts is important. So too is ensuring that the belts are attached to the x-carriage by looping back around on themselves teeth to teeth, to prevent slipping.***

| **Parts** | **Shorthand Name**                    |**QUANTITY**|
|-----------|----------------------------------------|-------------|
| **Printed** |                                      |             |
| LEC_007_P_01_TOP-CORNER_L | TOP-CORNER_L           | 1           |
| LEC_007_P_02_TOP-CORNER_R | TOP-CORNER_R           | 1           |
| LEC_007_P_03_Z-AXIS-CARRIAGE-LOWER | Z-AXIS-CARRIAGE-LOWER | 1   |
| **Components** |                                    |             |
| LEC_007_C_GT2-BELT | GT2-BELT                       | 2 |
| **Fixings** |                                       |             |
| LEC_007_F_01_M2.5-10MM_BUTTONHEAD-SCREW | M2.5-10MM-BUTTONHEAD-SCREW  | 4 |
| LEC_007_F_03_M2.5-12MM_BUTTONHEAD-SCREW | M2.5-12MM-BUTTONHEAD-SCREW   | 4 |
| LEC_007_F_06_M3-18MM-BUTTONHEAD-SCREW | M3_18MM-BUTTONHEAD-SCREW | 4 |
| LEC_007_F_01_M3-35MM-SOCKETHEAD-SCREW | M3_35MM-SOCKETHEAD-SCREW | 6 |
| LEC_007_F_02_M5-10MM-SOCKETHEAD-SCREW | M5_10MM-SOCKETHEAD-SCREW | 2 |
| LEC_007_F_03_M5-SLIDE-NUT | M5_SLIDE-NUT            | 6           |
| LEC_007_F_04_CABLE-TIE-5MM | CABLE-TIE-5MM          | 8           |

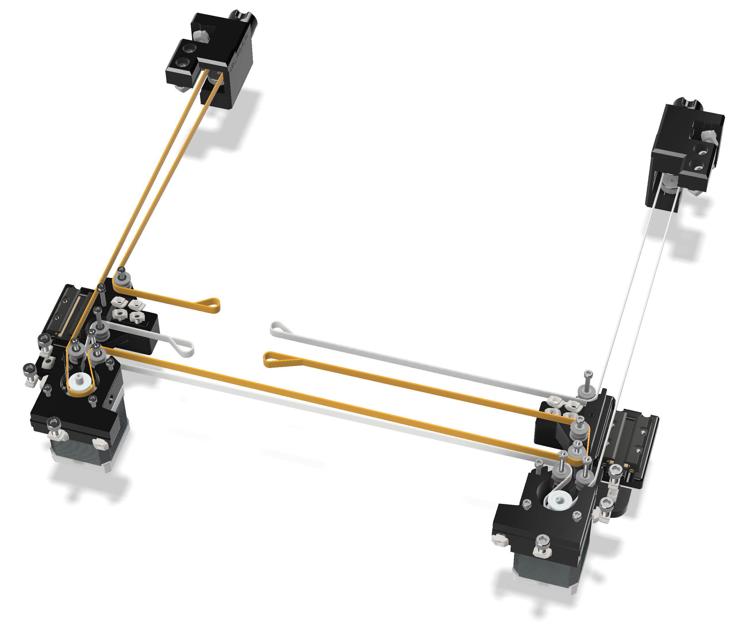
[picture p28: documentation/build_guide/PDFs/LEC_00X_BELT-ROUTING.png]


***FIGURE 8.0. Belt routing with top front corner parts removed for clarity, and belts coloured to aid clarity. Belts attach to the x-carriage*** 

***NOTE: Each belt, loops through the belt tensioners at the back of the instrument. Once the belt has followed the path, loop around the carriage in the same way as for the other end. At this stage, make sure that the belt tensioner is inserted into the rear of the instrument, and the tensioner knob is screwed on loosely. This is important, to ensure sufficient belt before cutting. Pull the belt tight with a pair of pliers along its route and then secure with a cable tie. Now you can cut the belt.***

**8.1** You should start with two **GT2-BELTS**. Take one end, and pass it through the hole on the Z-carriage constructed in step **23**, and loop it back on itself. The teeth of the **GT2-BELT** should lock into eachother. Secure this in place using two **CABLE-TIE-5mm**. Do the same with the second belt on the opposite end of the carriage. Route the belts through the front corner, Y carriage and back corners as per the diagram, and secure each belt to the back of the z-carriage using the same method described earlier in this step. When routing the belts through the Y-carriage, you may need to use a pair of tweezers to pull the belt through. 

**8.2** Now the belts have been routed and attached to the Z-axis carriage, attach the Z-axis carriage to the upper rail carriage on the upper X rail using **M2.5_12mm_BUTTONHEAD-SCREW**. Screw the **Z-AXIS-CARRIAGE-LOWER**  to the lower rail carriage using **M2.5_10mm_BUTTONHEAD-SCREW**. The **Z-AXIS-CARRIAGE-LOWER** is also screwed to the Z-carriage constructed in step **23** using **M3_18mm_BUTTONHEAD-SCREW**. 

**8.3**ADD STEP TO ATTACH THE FRONT CORNERS. LEFT HAND SIDE NEEDS SMALLER M3 SCREWS TO ATTACH STEPPER MOTORS, 35MM CURRENTLY TOO LONG. IDEALLY NEED 30MM. 

**8.4** Once the belts and Z-carriage are in place, tighten the belts using the back corner knobs constructed in step **10**. 

***The belt should then be tightened, by using the tensioner knobs at the back of the instrument, pulling the belts backwards. They should be sufficiently tight so as not to be sagging, but not 'guitar string' tight.***

-----------------
### 9.0 Z-AXIS
-----------------

***The z-carriage carries the optics - including the camera, lens and light, and enables movement up and down. The carriage is mounted on the x-carriage and slides up and down on rods, driven by a leadscrew attached to the z-axis stepper motor***

| **Parts** | **Shorthand Name**                    |**QUANTITY**|
|-----------|----------------------------------------|-------------|
| ***Printed*** |                                    |             |
| LEC_008_P_01_Z-CARRIAGE | Z-CARRIAGE               | 1           |
| LEC_008_P_02_LIGHT-BRACKET-TOP | LIGHT-BRACKET-TOP | 1           |
| LEC_008_P_03_LIGHT-BRACKET-BOTTOM | LIGHT-BRACKET-BOTTOM | 1     |
| LEC_008_P_04_OPTICS-MOUNT | OPTICS-MOUNT           | 1           |
| LEC_008_P_05_CAM-MOUNT | CAM-MOUNT                 | 1           |
| LEC_008_P_06_RAIL-INSERT | RAIL-INSERT             | 1           |
| LEC_008_P_07_OPTIC-SCREW | OPTIC-SCREW             | 1           |
| LEC_008_P_08_ZLIM-TRIGGER | ZLIM-TRIGGER           | 1           |
| LEC_008_P_09_BACK-ROD-SECURE | BACK-ROD-SECURE     | 2          |
| LEC_008_P_10_FRONT-ROD-SECURE | FRONT-ROD-SECURE   | 2          |
| LEC_008_P_11_LIGHT-MOUNT | LIGHT-MOUNT             | 1           |
| LEC_008_P_12_LIGHT-KNOB | LIGHT-KNOB               | 1           |
| LEC_008_P_13_LIGHT-DIFFUSER | LIGHT-DIFFUSER       | 1           |
| LEC_008_P_14_LIGHT-SLIDER | LIGHT-SLIDER       | 1           |
| ***Components*** |                                 |             |
| LEC_008_C_01_Z-STEPPER | Z-STEPPER                 | 1           |
| LEC_008_C_02_CAM | CAM                             | 1           |
| LEC_008_C_03_CAM-HDMI | CAM-HDMI                             | 1      |
| LEC_008_C_04_LENS | LENS                           | 1           |
| LEC_008_C_05_KFL08 | KFL08-BEARING                 | 1           |
| LEC_008_C_06_FLEX-COUPLING | FLEX-COUPLING         | 1           |
| LEC_008_C_07_Z-SCREW | Z-SCREW                     | 1           |
| LEC_008_C_08_F-ROD | F-ROD                         | 2           |
| LEC_008_C_09_R-ROD | R-ROD                         | 2           |
| LEC_008_C_10_LED-RING | LED-RING                   | 1           |
| LEC_008_C_11_Z-LEADSCREW | LEADSCREW                   | 1           |
| ***Fixings*** |                                    |             |
| LEC_008_F_01_M2.5-10MM-SOCKETHEAD-SCREW | M2.5-10MM-SOCKETHEAD-SCREW   | 4 |
| LEC_008_F_02_M3-10MM-SOCKETHEAD-SCREW | M3-10MM-SOCKETHEAD-SCREW       | 3 |
| LEC_008_F_03_M3-12MM-SOCKETHEAD-SCREW | M3-12MM-SOCKETHEAD-SCREW | 11|
| LEC_008_F_04_M3-HEX-NUT | M3-HEX-NUT               | 8           |
| LEC_008_F_05_M5-10MM-SOCKETHEAD-SCREW | M5-10MM-SOCKETHEAD-SCREW | 2 |
| LEC_008_F_06_M5-HEX-NUT | M5-HEX-NUT               | 2           |
| LEC_008_F_06_M2.5-12MM | M2.5-12MM-SOCK-SCREW               | 2     |

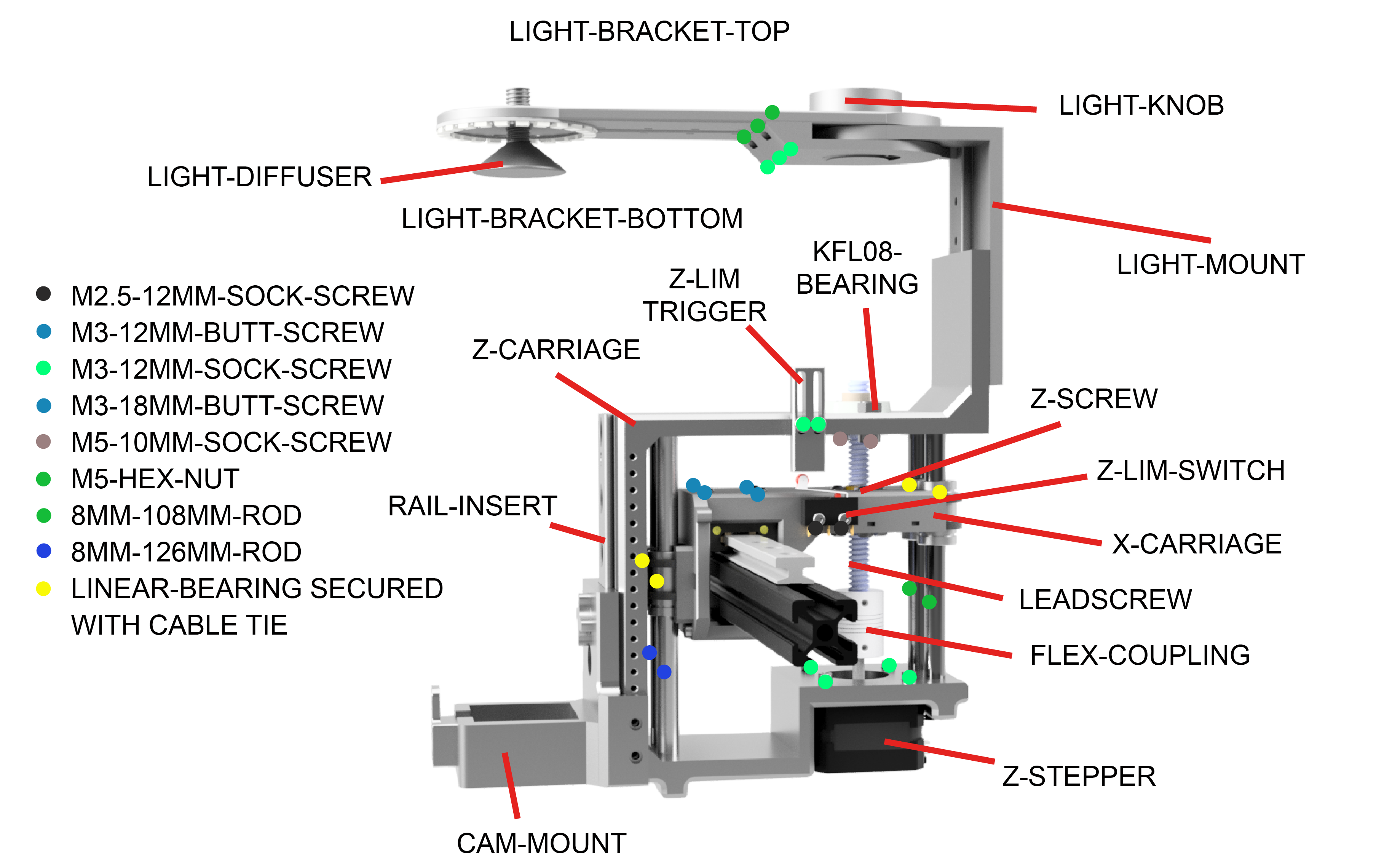
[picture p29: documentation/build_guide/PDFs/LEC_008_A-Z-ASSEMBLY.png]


**FIGURE 9.0. Z-axis assembly** 



**FIGURE 9.1 Z-axis assembly 2**

**9.1** Start by attaching various printed parts and components to the **Z-CARRIAGE**. Start by screwing the **RAIL-INSERT** to the **Z-CARRIAGE** using **M3_12mm_SOCKETHEAD-SCREW**. Next, attach the **ZLIM-TRIGGER** using **M3_12mm_SOCKETHEAD-SCREW**, attach the **KFL08** using **M5_10mm_SOCKETHEAD-SCREW** and **M5_HEX-NUT**, and attach the **Z-STEPPER** using **M3_12mm_SOCKETHEAD-SCREW**. Finally, attach the **FLEX-COUPLING** to the drive shaft of the **Z-STEPPER**, which should be secured using ..

**9.2**. Next, we need to attach the **Z-CARRIAGE** to the Z-carriage on the X-rail. To do this, orient the **Z-CARRIAGE** as per the diagram, and pass the two **F-ROD** (longer rods) through the holes on the front underside of the **Z-CARRIAGE**. The rods need to pass through the linear bearings attached to the Z-carriage on the Z-rail, before slotting into the grooves on the underside of the top face of the **Z-CARRIAGE**. Gently tap these into place, and screw in the **FRONT-ROD-SECURE** to secure these rods in place. Do the same for the **R-ROD** (shorter rods) and secure these using **BACK-ROD-SECURE**. Finally, pass the **Z-SCREW** through the **KFL08** and screw it into the **FLEX-COUPLING**. Secure this in place by screwing the **Z-SCREW** into the **KFL08**. Gently turning the **FLEX-COUPLING** should now move the **Z-CARRIAGE** up and down. 

**9.3** Next, attach the **OPTICS-MOUNT** and **LIGHT-MOUNT** by slotting them into the front and of the **Z-CARRIAGE** respectively. Screw the **OPTIC-SCREW** into the **CAM-MOUNT**, and screw the **CAM-MOUNT** into the **CAM-MOUNT** using **M2.5_10mm_SOCKETHEAD-SCREW**. 

**9.4** Finally, assemble the bracket for the light ring. Attach the **LIGHT-BRACKET-TOP** to the **LIGHT-BRACKET-BOTTOM** using **M3_10mm_SOCKETHEAD-SCREW** and **M3_HEX-NUT**. Leave this assembly to one side for now, as we need to solder and wire up the light ring before attaching it to the **LIGHT-MOUNT**. 

-----------------
### 10.0 ELECTRONICS
-----------------

***The electronics of the LabEmbryoCam are concentrated in the electronics enclosure mounted on the rear of the instrument. A number of wiring looms and individual cables, connect this to different parts of the instrument, via labelled ports on the electronics enclosure***

| **PARTS** | **SHORTHAND NAME**                       |**QUANTITY**|
| ----------|------------------------------------------|-------------|
| ***3D PRINTED*** |                                      |             |
| LEC_009_P_01_MOUNTING-PLATE | MOUNTING-PLATE         | 1           |
| LEC_009_P_02_PORT-PLATE | PORT-PLATE         | 1           |
| LEC_009_P_03_FAN-PLATE | FAN-PLATE         | 1           |
| LEC_009_P_04_FRONT-BREAKOUT-MOUNT | FRONT-BOARD-MOUNT        | 1      |
| LEC_009_P_05_CABLE-MOUNT | CABLE-MOUNT         | 8          |
| LEC_009_P_06_R-FRONT-PANEL | R-FRONT-PANEL         | 1          |
| LEC_009_P_07_L-FRONT-PANEL | L-FRONT-PANEL         | 1          |
| LEC_009_P_08_ELEC-MOUNT-BOTTOM | BOTTOM-ENCLOSURE-BRACKET | 1   |
| LEC_009_P_09_ELEC-MOUNT-TOP | TOP-ENCLOSURE-BRACKET| 1          |
| LEC_009_P_10_MICROCONTROLLER-BRACKET | MICROCONTROLLER-BRACKET| 1     |
| LEC_009_P_11_DISPLAY-FASCIA | DISPLAY-FASCIA| 1          |
| LEC_009_P_12_DISPLAY-REAR | DISPLAY-REAR| 1          |
| LEC_009_P_13_DISPLAY-ARM | DISPLAY-ARM| 1          |
| LEC_009_P_14_DISPLAY-BRACKET | DISPLAY-BRACKET| 1          |
| LEC_009_P_15_CABLE-BRACKET | CABLE-BRACKET| 10          |
| LEC_009_P_16_Y-LIM-SWITCH-MOUNT | Y-LIM-SWITCH-MOUNT| 1          |
| ***COMPONENTS*** |                                  |             |
| LEC_009_C_01_THOR-ELEC-ENC | ELECTRONICS-ENCLOSURE | 1       |
| LEC_009_C_02_THOR_ELEC-ENC-BASEPLATE | ELECTRONICS-BASE-PLATE| 1    |
| LEC_009_C_03_RPI4 | RPI4                             | 1            |
| LEC_009_C_04_USB-HUB | USB-HUB                       | 1            |
| LEC_009_C_05_PSU-SEASONIC300SUG | PSU-SEASONIC300SUG | 1            |
| LEC_009_C_06_DUET | DUET                             | 1            |
| LEC_009_C_07_ARDUINO | ARDUINO                       | 1            |
| LEC_009_C_08_RJ45-CONN | RJ45-CONN                   | 1            |
| LEC_009_C_09_SWITCH | SWITCH                         | 1            |
| LEC_009_C_10_HDMI-CONN | HDMI-CONN                   | 2            |
| LEC_009_C_11_USB-CONN | USB-CONN                     | 3           |
| LEC_009_C_12_DB15-M-CONN | DB15-M-CONN               | 1            |
| LEC_009_C_13_DB25-M-CONN | DB25-M-CONN               | 1            |
| LEC_009_C_14_ATX-BREAKOUT | ATX-BREAKOUT             | 1            |
| LEC_009_C_15_CASE-FAN | CASE-FAN                       | 1            |
| LEC_009_C_16_RPI_FAN | RPI_FAN                       | 1    |
| LEC_009_C_17_CSI-HDMI-CAM-HAT | CAM-HAT                | 1            |
| LEC_009_C_18_RPI-HQ-CAM | CAM                | 1            |
| LEC_009_C_19_LENS | LENS                | 1            |
| LEC_009_C_20_HDMI-F-F-COUPLER | HDMI-COUPLER         | 1            |
| LEC_009_C_21_USB-C-R-ANGLE-CABLE | USB-C-R-ANG         | 2            |
| LEC_009_C_22_MICRO-HDMI-R-ANGLE-CABLE | U-HDMI-CABLE  | 1            |
| LEC_009_C_23_USD-CARD | USD-CARD  | 1            |
| LEC_009_C_24_USBA-ARDUINO | ARD-USB  | 1            |
| LEC_009_C_25_USBMIC-DUET | DUET-USB  | 1            |
| LEC_009_C_26_DISPLAY-HDMI | DISP-HDMI  | 1            |
| LEC_009_C_27_DISPLAY-USB | DISP-USB  | 1            |
| LEC_009_C_28_DISPLAY | DISPLAY  | 1            |
| LEC_009_C_28_JOYSTICK | JOYSTICK  | 1            |
| LEC_009_C_28_Z-BUTTONS | Z-BUTTONS  | 2            |
| ***FIXINGS*** |      |      |
| LEC_009_F_01_M3_12mm_COUNTERSUNK-SCREW | M3_12mm_COUNTERSUNK-SCREW | 3 
| LEC_009_F_02_M3_DB-JACK-SCREW-HEAD | JACK-SCREW | 4    |
| LEC_009_F_03_M3_NYLOC-NUT | NYLOC-SCREW | 4    |
| LEC_009_F_04_M3_USB-SCREWS | NYLOC-SCREW | 1    |
| LEC_009_F_05_TRIPOD-SCREW | CAM-SCREW | 1    |
| LEC_009_F_06_M4-HEX-40MM-SCREW | DISPLAY-HEX-SCREW | 2    |
| LEC_009_F_07_M4-NYLOC-HEX-NUT | DISPLAY-HEX-NUT | 2    |
| LEC_009_F_08_M2.5-8MM-SOCKETHEAD-SCREW | DISPLAY-M2.5-SOCKETHEAD | 4  |
| LEC_009_F_09_M5-6MM-BUTTONHEAD-SCREW | DISPLAY-M5-BUTTONHEAD | 4    |
| LEC_009_F_10_M3-8MM-SOCKETHEAD-SCREW | DISPLAY-M3-SOCKETHEAD | 4    |
| LEC_009_F_11_M5-6MM-BUTTONHEAD-SCREW | CABLE-BRACKET-M5-BUTTONHEAD |10| | LEC_009_F_12_M5-SLIDENUT | M5-SLIDENUT | 14   |
| ***ELECTRONICS ASSEMBLIES*** |      |      |
| LEC_009_A_01_ELEC-ENC | ELECTRONICS-ENCLOSURE | 1    |
| LEC_009_A_02_25PIN-M-ELEC-ENC | 25PIN-ENC | 1    |
| LEC_009_A_03_25PIN-F-EXT | 25PIN-EXT | 1    |
| LEC_009_A_04_15PIN-M-ELEC-ENC | 15PIN-ENC | 1    |
| LEC_009_A_05_15PIN-F-EXT | 15PIN-EXT | 1    |
| LEC_009_A_06_FRONT-BOARD-ASSEMBLY | FRONT-BOARD | 1    |
| LEC_009_A_07_Z-BOARD-ASSEMBLY | Z-BOARD | 1    |

### 10.1 Overview
The LabEmbryoCam build requires six wiring looms, which are treated here as 'assemblies'. 
1. 25 pin wiring loom
    a) Inside the electronics enclosure (25PIN-EXT, 11.X)
    b) From the electronics enclosure to the front panel (25PIN-ELEC-ENC, 11.X)
    c) Front circuitboard assembly (FRONT-BOARD 11.X)
2. 15 pin wiring loom 
    a) Inside the electronics enclosure (15PIN-EXT, 11.X)
    b) From the electronics enclosure to the front panel (15PIN-ELEC-ENC, 11.X)
    c) Z-axis circuitboard assembly (Z-BOARD, 11.X)

For most builders, these will have been provided as already built 'assemblies', and can simply be attached to the relevant parts of the instrument. Nonetheless, for the assembly to be complete, the full details of how to create these wiring assemblies are provided at the end of the electronics section of the build guide, in the sections given for each part above.

-------------------
### 10.2 Electronics Enclosure
-----------------

***Electronics are mounted inside a metal enclosure, with 3D printed endplates, which is attached to the rear of the instrument.***



**FIGURE 10.0**

## Electronics Enclosure (LEC_009_A_01)



**FIGURE 10.1** Electronics enclosure assembly

----
### 10.3 Attaching Internal Components
------

Connect the 3D printed plastic MOUNTING-PLATE to the metal plate of the electronics enclosure. Using M3 XX mm screws.

Begin by attaching the power supply, PSU-SEASONIC300SUG, with four screws - two to attach it to the front panel, and two to attach the back to the MOUNTING plate.

Attach the FAN to the rear fan plate of the electronics enclosure, using the four fan screws, included with it.

Install the USB-HUB using xx MM screws, with the USB-A ports facing the fan, and the USB-C ports facing the PSU.

Attach the ATX-BREAKOUT to the MOUNTING-PLATE using XX MM screws.

Connect the ARDUCAM HDMI-CSI adapter to the top of the RPI4, and then the RPI to the MOUNTING-PLATE, using M2.5 screws.

...FIG..

---------------
### 10.4 Wiring Loom
---------------



**FIGURE 10.2 ** Wiring loom

Two wiring looms connect the majority of the electronic components in the LabEmbryoCam to the electronics enclosure on the rear of the instrument.

Begin by cutting the wires detailed below to the necessary lengths, for each of the looms. Each wire must be terminated with the appropriate conncetion types, and labelled acording to the guide below.

### 10.5 **Wiring Loom 1 - DB25**

***Runs from front of instrument and terminates to a DB25 female connector, that connects to the receptive male port on the electronics enclosure***

| WIRES REQUIRED     |         |             |
| ------------------ |         |  ---------- |
| **Wire type**      |**Function**         |  **Length** |
| 4 Multicore ribbon | X_Stepper_Motor |  100cm      |
| *BLACK* |  |      |
| *BLUE* |  |       |
| *GREEN* |  |        |
| *RED* |  |        |
| 4 Multicore ribbon | Y_Stepper_Motor | 65cm      |
| *BLACK* |  |      |
| *BLUE* |  |       |
| *GREEN* |  |        |
| *RED* |  |        |
| 2 Multicore ribbon | Y_Limit_Switch |  50cm     |
| *BLUE* |  |      |
| *YELLOW* |  |       |
| 2 Multicore ribbon | X_Limit_Switch |  50cm   |
| *BLUE* |  |      |
| *YELLOW* |  |       |

### 10.6 **Front Panel Wiring Hub**

-- change z-but colours


**FIGURE 10.3**


***FIGURE 10.4** FRONT PANEL BREAKOUT ...

-----------
#### 10.7 **Wiring Loom 2 - DB15**
-----------

***Runs from Z-carriage to a DB15 female connector, that connects to the receptive male port on the electronics enclosure***

| WIRES REQUIRED     |                 |            |
| ------------------ | --------------- | ---------- |
| **Wire type**      | **Function**    | **Length** |
| 4 Multicore ribbon | Z_Stepper_Motor | 85cm       |
| 2 Multicore ribbon | Z_Limit_Switch  | 50cm       |
| 4 Multicore ribbon | LED             | 50cm       |

| WIRES REQUIRED                             |              |            |                   |
| ------------------------------------------ | ------------ | ---------- | ----------------- |
| **Wire type**                              | **Function** | **Length** | **Termination A** |
| 4 Multicore ribbon                         | LED          | 50cm       | BARE              |
| 2 Multicore ribbon                         | Z-limit      |            | 25cm              |
| ** double check these z-carriage lengths** |              |            |                   |

Black, Blue, Green, Red

**diagram/lengths needed**

-----------
### 10.8 **Z Wiring Hub**
-----------


***FIGURE 10.5**. Z-AXIS-BREAKOUT

**diagram/lengths needed**

-----------
### 10.9 Electronics Enclosure Wiring
---------------

| WIRES REQUIRED       |Function  |Length |Termination	|Routing|
| -------------------- | ---- |---| --- | ---|
|***DB25*** | | | | |
| 4 Multicore ribbon   | X Stepper motor| 20cm |Wire -> MOLEX|DB25->DUET|
| 4 Multicore ribbon   | Y Stepper motor|  20cm |Wire -> MOLEX|DB25->DUET|
| 1 x Blue, 1 x Yellow | X Limit switch|  25cm |Wire -> MOLEX|DB25->DUET|
| 1 x Blue, 1 x Yellow | Y Limit switch|  25cm |Wire -> MOLEX|DB25->DUET|
| 4 Multicore ribbon   | Z buttons|  20cm |Wire -> Wire| DB25->ARDUINO|
| 3 Multicore ribbon   | X Joystick|  20cm  |Wire -> Wire|DB25->ARDUINO|
| 3 Multicore ribbon   | Y Joystick|  20cm  |Wire -> Wire|DB25->ARDUINO|
|***DB15*** | | | | |
| 1 x Blue, 1 x Yellow | Z Limit switch|  25cm |Wire -> MOLEX|DB15->DUET|
| 4 Multicore ribbon   | Z Stepper motor|  20cm |Wire -> MOLEX|DB15->DUET|
| 4 Multicore ribbon   | LED | 20cm |Wire -> MOLEX|DB15->ARDUINO|
| **Integrated Cables**       |   |      |        |          |
| HDMI   | Camera signal|  XX  |HDMI->HDMI|UPPER_HDMI_PORT->PI-CSI_BOARD|
| HDMI   | Control panel|  XX  |HDMI->HDMI|LOWER_HDMI_PORT->RPI4 MICROHDMI|
| USB   | Solid State Drive|  XX  |USB->USB|USB PORT->RPI-USB3|
| USB   | Accessory|  XX  |USB->USB|USB PORT->USB-HUB|
| ETHERNET   | Networking|  XX  |RJ45->RJ45|RJ45-PORT->RPI4-RJ45|

Up/down buttons

RG - up

BB - down 

direction on circuit board needs changing..? or microcontroller?

### Cooling..

-----------------
## 12.0 VIBRATION-INSULATION
-----------------

The bottom corners should be attached to the instrument towards the end of the build, to prevent damage during the build process. 

Each corner encompasses two vibration insulation components - a sorbothene foot, and a 3D printed leafspring. Once assembled, care should be taken not to apply too much pressure onto the instrument.

| **Parts**                             | **Shorthand Name**       | **QUANTITY** |
| ------------------------------------- | ------------------------ | ------------ |
| ***Printed***                         |                          |              |
| LEC_002_P_01_FR/BL-BOTTOM-CORNER      | FR/BL_BOTTOM-CORNER      | 2            |
| LEC_002_P_01_FR/BR-BOTTOM-CORNER      | FR/BR_BOTTOM-CORNER      | 2            |
| LEC_002_P_03_LEAFSPRING               | LEAFSPRING               | 4            |
| ***Components***                      |                          |              |
| LEC_002_C_01_SORBOTHENE-FEET          | SORBOTHENE-FEET          | 4            |
| ***Fixings***                         |                          |              |
| LEC_002_F_01_M5_10MM-BUTTONHEAD-SCREW | M5_10MM-BUTTONHEAD-SCREW | 12           |
| LEC_002_F_02_M5-SLIDE-NUT             | M5_SLIDE-NUT             | 12           |
| LEC_002_F_03_M6-12MM_BUTTONHEAD-SCREW | M6_12MM-BUTTONHEAD-SCREW | 4            |
| LEC_002_F_04_M6-45MM_BUTTONHEAD-SCREW | M6_45MM-BUTTONHEAD-SCREW | 4            |
| LEC_002_F_05_M6-HEX-NUT               | M6_HEX-NUT               | 4            |


**FIGURE 12.0**

**12.1** The bottom corners are attached to the base of the frame and are required to attach components used to insulate against vibrations, that may cause interference with acquired video footage. Start by attaching the 2 **FR/BL_BOTTOM-CORNER** and 2 **FR/BR_BOTTOM_CORNER** pieces to the underside corners of the assembled frame, using **M5_10mm_BUTTONHEAD-SCREWS** and **M5_SLIDE-NUTS**. 

**12.2** Next, construct the vibration insulating feet to each of the bottom corners. Start by screwing the **SORBOTHENE-FEET** to the **LEAFSPRING** using **M6_12mm_BUTTONHEAD-SCREWS**. Then place **M6_HEX-NUTS** into the grooves within each **LEAFSPRING**. Screw in each of the assembled feet into the bottom corner pieces, using the **M6_HEX-NUTS** and **M6_45mm_BUTTONHEAD-SCREWS**. 

-----------------

### Panel attachment

-----------------

While not essential, attaching plastic panels to the LabEmbryoCam is encouraged as for little cost, they help to keep the instrument clean, protect moving parts and cables and they keep it looking tidy. Note the size of the panels required in the bill of materials and their 
locations above. Before installing the panels, insert M3 square nuts into the holes at the top and bottom of each spacer. The square nuts should slide as far as they can be pushed, using a small allen key or similar, so that the hole in the nut aligns with the hole in the 3D printed spacer.

-----------------
### Manual Controls
---------------

| PARTS REQUIRED                          |                 |
|-----------------------------------------|-----------------|
|**Component description**               |**Qty required** |
| Red wire                                | 755 cm          |
| Green wire                              | 520 cm          |
| Blue wire                               | 620cm           |
| Black wire                              | 595 cm          |
| Yellow wire                             | 350 cm          |
| White wire                              | 325 cm          |
| XY Joysticks                            | 1               |
| Z axis buttons                          | 2               |
| **3D Prints**                           |                 |
| Joystick_panel_right                    | 1               |
| Joystick_panel_left                     | 1               |

Once the joystick and buttons are attached to the front panels, the front panels can then be attached to the LabEmbryoCam.

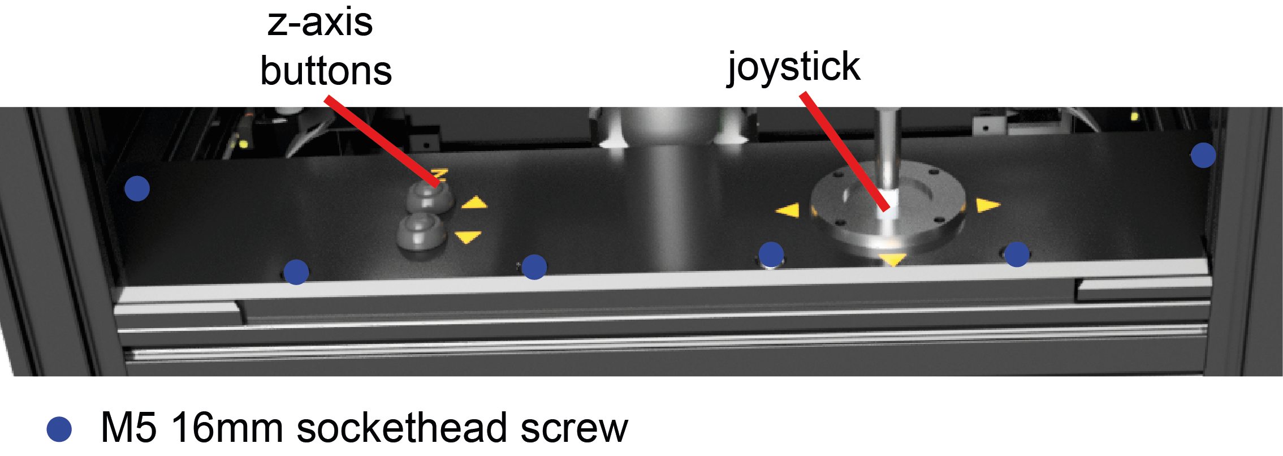
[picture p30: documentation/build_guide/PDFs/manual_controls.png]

**FIGURE 12.0**

Solder cables to each of the pins on the joystick (2 x 3 cables per axis), and two buttons (2 x 2 cables) and 
then attach the buttons and joystick to the 3D printed front panels. Ensure the cables are labelled to ensure they can be connected 
appropriately to the microcontroller. 

.. note:: Although not essential, joystick and button labels are provided as seperate STLs and can be printed in different colour filaments i.e. begin the print with the label colour, before switching to the colour used for the main body of the part. 

-----------------
### DISPLAY INSTALLATION
-----------------

--------------
### Display installation
------------------
| **Parts**                             | **Shorthand Name**       | **QUANTITY** |
| ------------------------------------- | ------------------------ | ------------ |
| ***Printed***                         |                          |              |
| LEC_002_P_XX      | XX      | 2            |
| LEC_002_P_XX     | XX      | 2            |
| LEC_002_P_03_LEAFSPRING               | LEAFSPRING               | 4            |

--------------
### 13.0 LID
------------------

***While not essential, the lid keeps the instrument clean and offers some protection from interference during an experiment***. 

| **PARTS** | **SHORTHAND NAME**                       |**QUANTITY**|
| ----------|------------------------------------------|-------------|
| ***COMPONENTS*** |                                      |             |
| LEC_010_C_01_HINGE | HINGE         | 2           |
| LEC_010_C_02_TOP-LID-PLASTIC-311X315 | TOP-LID-PLASTIC         | 1    |
| LEC_010_C_03_FRONT-LID-PLASTIC-315X59 | FRONT-LID-PLASTIC        | 1  |
| LEC_010_C_04_HANDLE | HANDLE        | 1  |
| LEC_010_C_05_CUBE-CONNECTORS | CUBE-CONNECTORS        | 6  |
| ***EXTRUSION*** |                                      |             |
| LEC_010_E_01_2020-312MM | 2020-312MM         | 2           |
| LEC_010_E_02_2020-303MM | 2020-303MM         | 3           |
| LEC_010_E_02_2020-60MM | 2020-60MM         | 2           |
| ***FIXINGS*** |                                      |             || |LEC_010_F_01_M5-SLIDENUT | M5-SLIDENUT        | 2  |
|LEC_010_F_01_M5-8MM-SOCKETHEAD-SCREW | M5-8MM-SOCKETHEAD-SCREW      |2|

--------------
## 14.0 TESTING
------------------

***This section is still a work in progress - with testing procedures.***

--------------
### 14.1 Duet Board Testing
------------------
The Duet XYZ board has a control interface not routinely used in the operation of the LEC, but useful during initial setup.

To access it, connect the board directly to a network connection via the ethernet port on the board itself (not the ethernet). Turn on the LEC, and navigate to the Terminal and type ``` cutecom```. 

This will open a window allowing us to determine the IP address of the Duet board on the network. Once open - choose the Device ```/dev/tty/ACMX```, with X usually being either 0, 1 or 2 from the dropdown.

Click 'Open'. If joystick or light is returned, this means you have selected the wrong Device - so try another.

Type ```M115``` and if all is working, you should see the current firmware version.

If so, type ```M552 S0```, followed by ```M552 S1``` to deactivate, and then reactivate the network connection.

You should see 'Network running. IP address = XXX.XXX.X.XXX', with the XXX corresponding to the address of your own instrument on your network.

You can now access the Duet board of the LabEmbryoCam on your network via this IP address, from any other device connected to the same network. You will be prompted for a password. The default password for LabEmbryoCams is ```radix```

--------------
## 14.0 TROUBLESHOOTING
------------------
### Vibrating and/or noisy stepper motor - but no movement
This is typically caused by a bad connection to the stepper motor caused by either a damaged cable, or incorrect wiring. If the instrument was previously working then incorrect wiring is unlikely. Consider a wholesale replacement of the DB-25 wiring loom. Before doing so, by opening the electronics enclosure you can directly connect the stepper motor to the Duet board to see if this resolves the issue  - if so, you can be assured that wiring is indeed the issue.

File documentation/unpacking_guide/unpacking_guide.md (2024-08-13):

# LabEmbryoCam Unpacking Guide

**This guide follows the steps required to assemble an LEC following receipt after shipping**

-----------------
### 1.0 UNPACKING
-----------------
The LEC can be removed from its packaging using the frame. Avoid using the 'internals' to pull it out, instead using the outer pieces of frame, and be mindful of snagged wires.

-----------------
### 2.0 ELECTRONICS MOUNTING
-----------------
Two 3D printed brackets must be attached to the rear of the instrument to support the LEC electronics enclosure. The lower of the two brackets includes a slot for mounting the data storage (SSD). Consult image below. The brackets are attached to the frame of the LEC using screws and slide nuts. Use the enclosed allen keys to tighten the slide nut up inside the slot and the electronics mounts will be locked in place. The LEC electronics enclosure brackets should be mounted centrally on the rear of the instrument.

Once the two brackets are installed, the LEC electronics enclosure can be slid in from the top of the instrument, with the ports at the bottom, and the fan vent facing upwards.

-----------------
### 3.0 DISPLAY MOUNTING
-----------------
The LEC uses a touch screen display, mounted to the front of the instrument, via an arm on a swivel. The bracket attached to the LEC frame will already be attached. Furthermore, the display will have the swivel arm already attached. Therefore, to fit the display to the frame requires first removing the hex-head screw and nut, aligning the arm, and then reinserting the screw, before tightening up the nut.

Once the LEC display is fitted, a USB-C cable, and HDMI cable must be attached to the display. The USB-C cable is tight. Run the HDMI and USB cables along the same route as the black cable bundle, and use the included cable ties to secure them.

-----------------
### 4.0 ATTACHING CAMERA AND LENS
-----------------
The camera and lens are shipped in the optics holder of the LEC. This slides on to the z-carriage from underneath and is intentionally stiff. The appropriate distance from the end of the lens to the sample holder will depend on the magnification used, and the choice of auxillary lens, which screws onto the end of the lens. A line will be marked on the z-carriage with black marker to indicate a good height to initially mount the optics holder. 

Once the optics holder is fitted, the included HDMI cable should be attached. The cable should be routed, following the same route as the other cables from the z-carriage in the cable bundle. Use the included cable ties to secure the HDMI cable alongside these other cables.

-----------------
### 5.0 ATTACHING CABLES
-----------------
The LEC electronics enclosure fascia has labelled ports. The USB and HDMI cables should be attached to the relevant labelled ports (DISP).

The LEC uses two custom cables - a 25 pin serial style cable, conneced to the X and Y stepper motors and Y, and Y limit switches, and a 15 pin serial style cable, connected to the Z stepper motor, Z limit switch and LED light. These cables have screws on either side, and should be screwed into the female recepticle on the port, to prevent the connector from falling out.

The power cable should be connected to the kettle style connector.

When running the LEC, data should be written to an external drive, preferrably an SSD (Solid State Drive). A cable is included  and the LEC will sit in the slot to the side of the electornics enclosure. The USB cable should be connected to the labelled 'SSD' slot on the electronics enclosure fascia. It is preferrable to attach the drive before powering on the instrument, as they will not always be detected if plugged in when the LEC is already powered up.

-----------------
### 6.0 FITTING FEET
-----------------
While the LEC can be used with the vibration insulating feet, experiments will inevitably be impacted by vibrations from the environment without them. Fitting them simply requires four screws to be attached. It is important to note that the feet are fragile. The 3D printed plastic leafspring parts will snap if excessive weight is placed on the instrument. For this reason, spare feet are provided and the sorbothene (rubber) part can be screwed onto a new 3D printed leafspring if required.

To fit the feet, lie the instrument on its side and use the included allen key to attach the screw the foot to the instrument using the included screws.

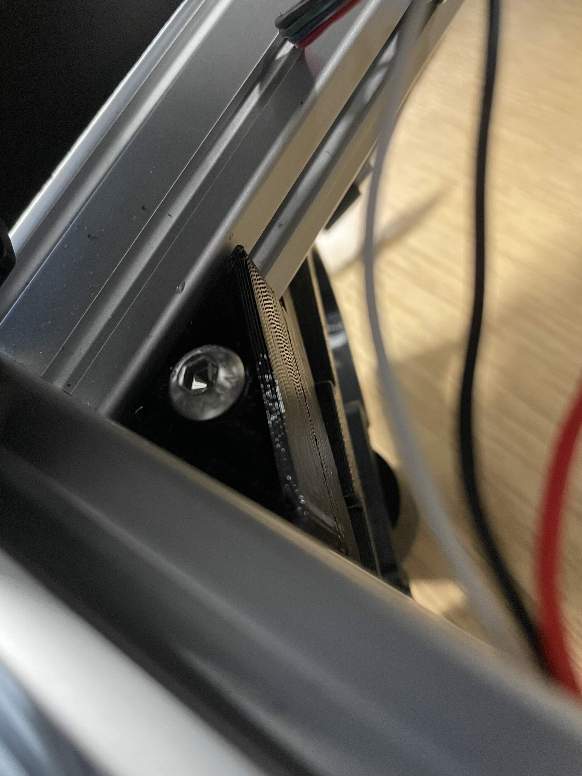
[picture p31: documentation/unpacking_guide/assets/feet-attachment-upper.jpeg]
 

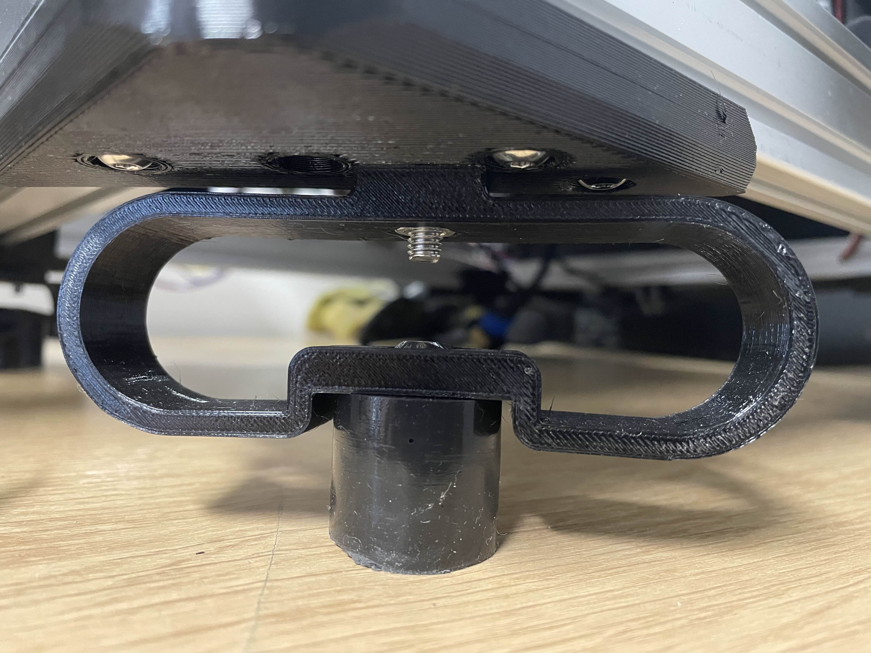
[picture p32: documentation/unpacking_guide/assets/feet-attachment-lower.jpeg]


-----------------
### 6.0 TURNING ON
-----------------
To turn the LEC on, use the ON/OFF toggle switch on the port end of the LEC. Follow the instructions in the USER MANUAL for operation of the LEC. However, given that this is the first operation post-shipping, a few things should be checked for.

i) Ensure that the cables at the bottom and rear of instrument have sufficient slack when attaching them to the cable holders with cable ties.

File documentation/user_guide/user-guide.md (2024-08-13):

# LabEmbryoCam User Guide



#### ***An opensource platform for automated measurement of developing animals. The LabEmbryoCam is a project originating with the EmbryoPhenomics research group at the University of Plymouth, UK. It has been made possible by support from UKRI, NERC, BBSRC and Plymouth Science Park.***

***Consider joining the Google Group https://groups.google.com/g/labembryocam. Doing so will help contribute to the advancement of this opensource project, and staying up-to date with updates and receiving support.***

-----------------
# INDEX
-----------------
* **1. HARDWARE SETUP**

* **2. USER INTERFACE**

* **3. XYZ CONTROLS AND SETTINGS**

* **4. CAMERA VIEW**

* **5. USING MANUAL CONTROLS TO FIND AND SAVE POSITIONS**

* **6. SETTING AND STARTING ACQUISITIONS**

* **7. NEXT STEPS**

-----------------

<center>THIS IS A LIVE DOCUMENT.</center>

<center>TO SEE THE MOST RECENT VERSION, SCAN THE QR CODE BELOW.</center>



-----------------
# 1. HARDWARE SETUP
-----------------
The LEC is a versatile multidimensional imaging platform. A broad range of magnifications are possible, using different optical hardware, particularly lenses. 

The distance between the sample and the lens will depend on the magnification and lens characteristics. Similarly, the optimum distance between the sample and the light will depend on the optical hardware, magnification, but also the sample type.

The LEC was initially developed for dark field imaging of developing aquatic embryos. Dark field imaging, in which a black background is achieved via lighting arriving at the sample from an oblique angle, works well for imaging developing embryos.

-----------------
# 2. USER INTERFACE
-----------------

Once you have powered on your system, you can enter the desktop environment of the LEC using the following password: `pi`. Once you have logged in, you can start the LabEmbryoCam (LEC) user interface by double clicking the icon on the desktop or in the Activities panel:



A terminal window will automatically open followed by the browser with the webserver (user interface) loaded. We can now proceed with getting the hardware set up for running an experiment. When the LEC user interface first loads, it connects to the various hardware components automatically - give it a few seconds before interacting with it to allow this process to complete.

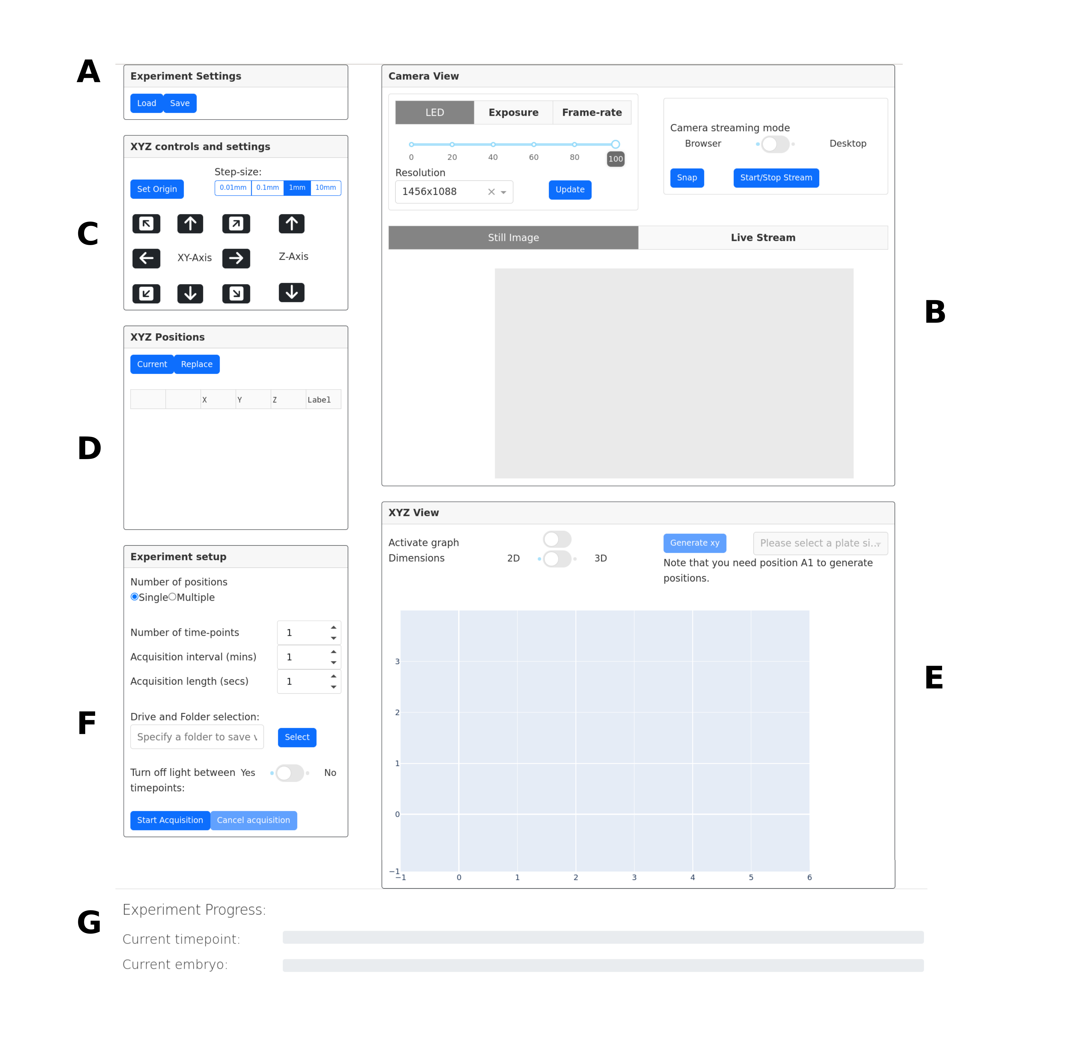
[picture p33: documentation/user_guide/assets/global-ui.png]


The LEC user interface is divided into a number of sections
* A) **Experiment Settings** - for loading a configuration file to repopulate previously used settings.
* B) **Camera View** - for adjusting the camera, streaming the camera feed, and snapping still images.
* C) **XYZ controls and settings** - for homing the XYZ stage, and moving the optics carriage around.
* D) **XYZ Positions** - for populating a list of XYZ positions.
* E) **XYZ View** - for interacting with XYZ positions, and automatically generating positions for wells of multiwell plates.
* F) **Experiment setup** - for configuring and running experiments - either at a single positon, or multiple.
* G) **Experiment Progress** - for monitoring the progress of an experiment.

-----------------
# 3. XYZ CONTROLS AND SETTINGS
-----------------
The first step required in setting up any experiment with the LEC is to home, or 'Set Origin' of the XYZ stage. This is essential to ensure that the correct origin is used when finding and creating positions and without doing this the XYZ stage will not be responsive. 

To home the stage, click the `Set Origin` button in the user interface.

***Before homing the stage, make sure there are no objects that could obstruct the movement of the stage - such as the lens being too high. Also, make sure not to use the app whilst the stage is homing as this could interfere with the process.***

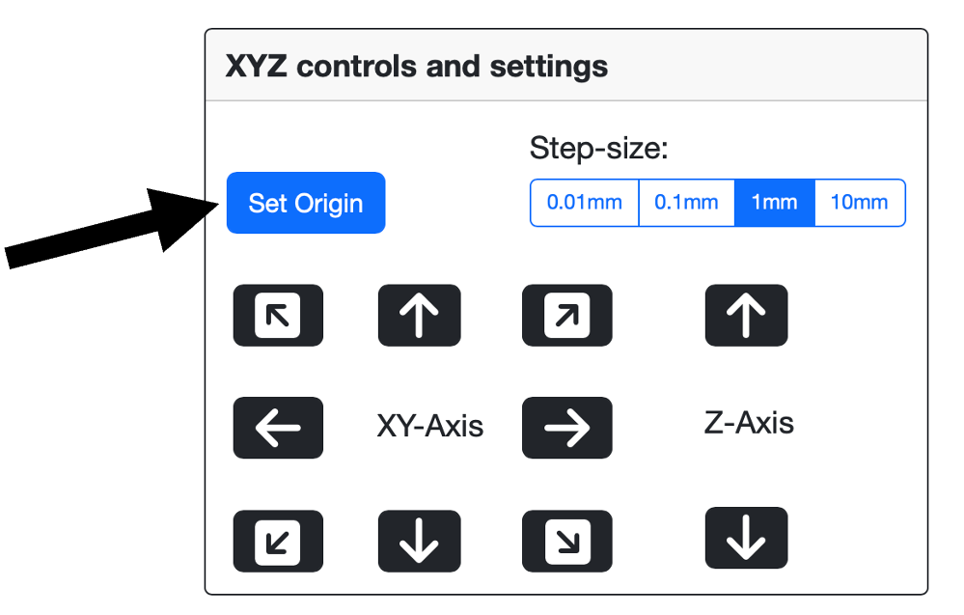
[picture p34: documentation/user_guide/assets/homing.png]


-----------------
# 4. CAMERA VIEW
-----------------
Camera and lighting settings will need adjusting to suit your experimental system - species, study aim etc.  

Adjusting the camera and lighting settings can simply be achieved using the `Camera View` section of the user interface: 

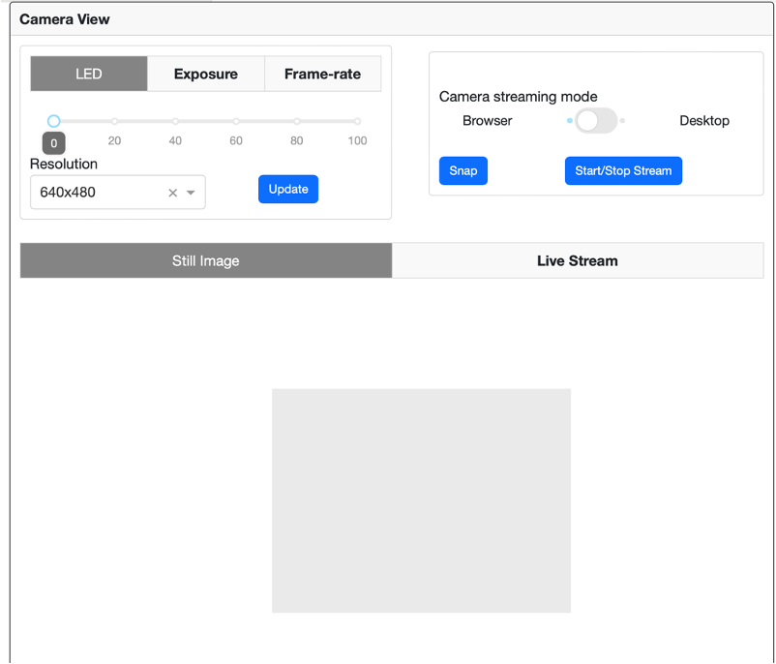
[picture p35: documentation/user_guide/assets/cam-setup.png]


Begin by choosing a resolution and these are dictated by the sensor modes available from the connected camera board. Currently there are two camera boards supplied with each LEC system: a global and a rolling shutter camera. The global shutter board only has one available sensor mode: 1456 x 1088 pixels @ 60 fps. The rolling shutter board has four different sensor modes: 1330 x 990 @ 120fps, 2028 x 1080 @ 50fps, 2028 x 1520 @ 40fps and 4032 x 3040 @ 10fps. Note that these framerates are a maximum achievable given low enough exposure times. 

A live stream can be initialised using 'Start/Stop Stream' - and a rotating cursor next to the button will indicate that the camera is running.

Use the live display to ascertain what changes, if any, may be required.

Note that the image you see, is smaller i.e. downsampled to fit on the display and to aid usability. You can Stop the stream and change to 'Desktop' if desired and when the stream is re-enabled a pop-up window will show you what the camera feed looks like in a larger window. You can also capture still images using the 'Snap' button, and these will be shown as interactive images in the 'Still Image' tab. 

You can then use the three tabs - LED, Exposure and Frame-rate, to make adjustments as required. However, changes to the camera's - exposure, frame rate, and resolution, should only be made when the 'Start/Stop Stream is deactivated. **Changes are only implemented when clicking 'Update'.**

The following are descriptions for each of the settings in the Camera View.
* **LED**: The percentage brightness of the LED ring light. Note that the lighting can also be adjusted by using the lighting mount up and down, and by screwing/unscrewing the darkfield adapter. The LED will by default go to sleep when not needed during an experiment.
* **Exposure**: The shutter speed at which the camera operates in milliseconds - 20 ms is a good starting point.
* **Analogue gain**: The analogue gain applied by the camera sensor, to be used too adjust the brightness of the images without affecting frame-rate. 
* **Frame-rate**: The frame-rate at which videos are captured, in frames per second.
* **Resolution**: Presets for resolution at which images will be captured - this is dependent on the available sensor modes for the connected camera board.

***For changes to the camera settings to take effect you must press the `Update` button at the bottom of the Camera Settings section.***

**Note**
There are two physical adjustable parameters on the lens itself, the iris and the magnification. The upper adjustment ring is for adjusting the magnification and the lower adjustment ring is for adjusting the iris. If you change the magnification, the required distance between the sample in the multiwell plate and the lens will need to be changed as well - higher magnification requires the lens to be closer to the sample, it will also result in a darker image and perhaps even a requirement for more light (either by choosing a longer exposure, increasing the brightness of the LED, or adjusting the physical position of the light). Finally, by opening or closing the iris, the depth of field (i.e. depth of the sample that is in focus) can be adjusted. Typically greater depth of field is very welcome, but it comes at the cost of a darker image. So, a compromise is required and will need to be decided on a case-by-case basis.

*Insert lense info here* **To do**

Two lenses are supplied with the LEC, a low magnification lens (specs) suitable for imaging whole wells in a multiwell plate and a higher magnification, variable zoom lens capable of imaging small specimens with the aid of auxillary lenses. The maximum field of view for the Hikrobot, low magnification lens is 83 x 62 mm (width x height), and the minimum field of view, i.e. at highest magnification, is 18 x 13.5 mm. By comparison, the higher magnification lens ...

Next to the 'Start/Stop Stream' button in the Camera View, is a 'Snap' button. This allows you to capture images dynamically while using the instrument. They are automatically saved in a 'snap-images' folder in the LEC application folder.

Still images are interactive, so you can zoom in and out, and move the image to find an improved view. Before starting the next step, you may wish to start the live video stream, if you haven't already, for easily finding the animals or subjects you wish to record using the LEC.

***If you would like to change the camera settings you must exit the live stream before doing this so that your changes can take effect. Then when you have finished choosing your desired setttings, press the `Update` button before starting the live stream again.***

-----------------
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

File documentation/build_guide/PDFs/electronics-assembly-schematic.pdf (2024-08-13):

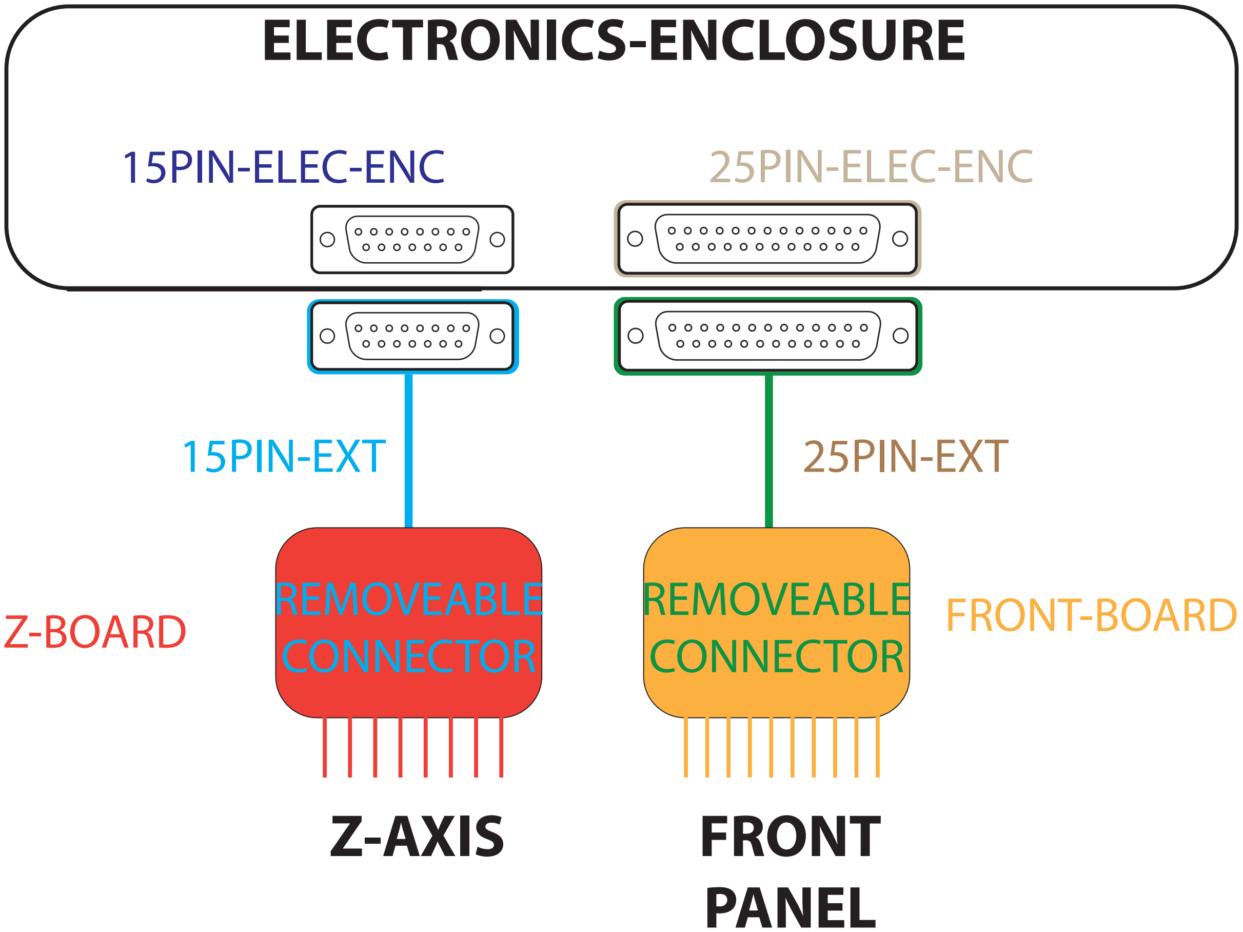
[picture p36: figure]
REMOVEABLE CONNECTOR; 25PIN-EXT; 15PIN-EXT; 15PIN-ELEC-ENC; FRONT-BOARD Z-BOARD; ELECTRONICS-ENCLOSURE; Z-AXIS; FRONT; PANEL; 25PIN-ELEC-ENC

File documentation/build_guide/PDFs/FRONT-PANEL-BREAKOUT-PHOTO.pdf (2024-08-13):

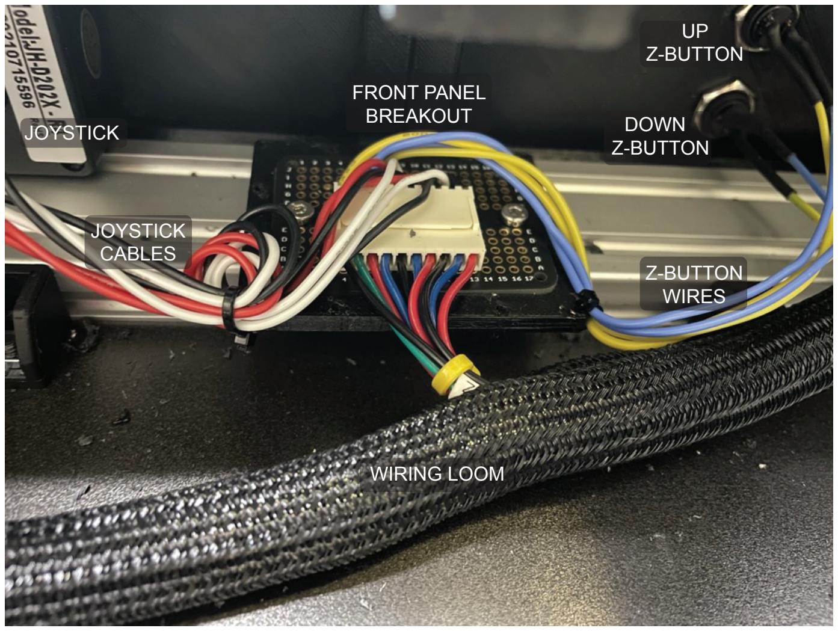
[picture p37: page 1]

JOYSTICK

FRONT PANEL
BREAKOUT

UP
Z-BUTTON

DOWN
Z-BUTTON

WIRING LOOM

Z-BUTTON
WIRES

JOYSTICK
CABLES

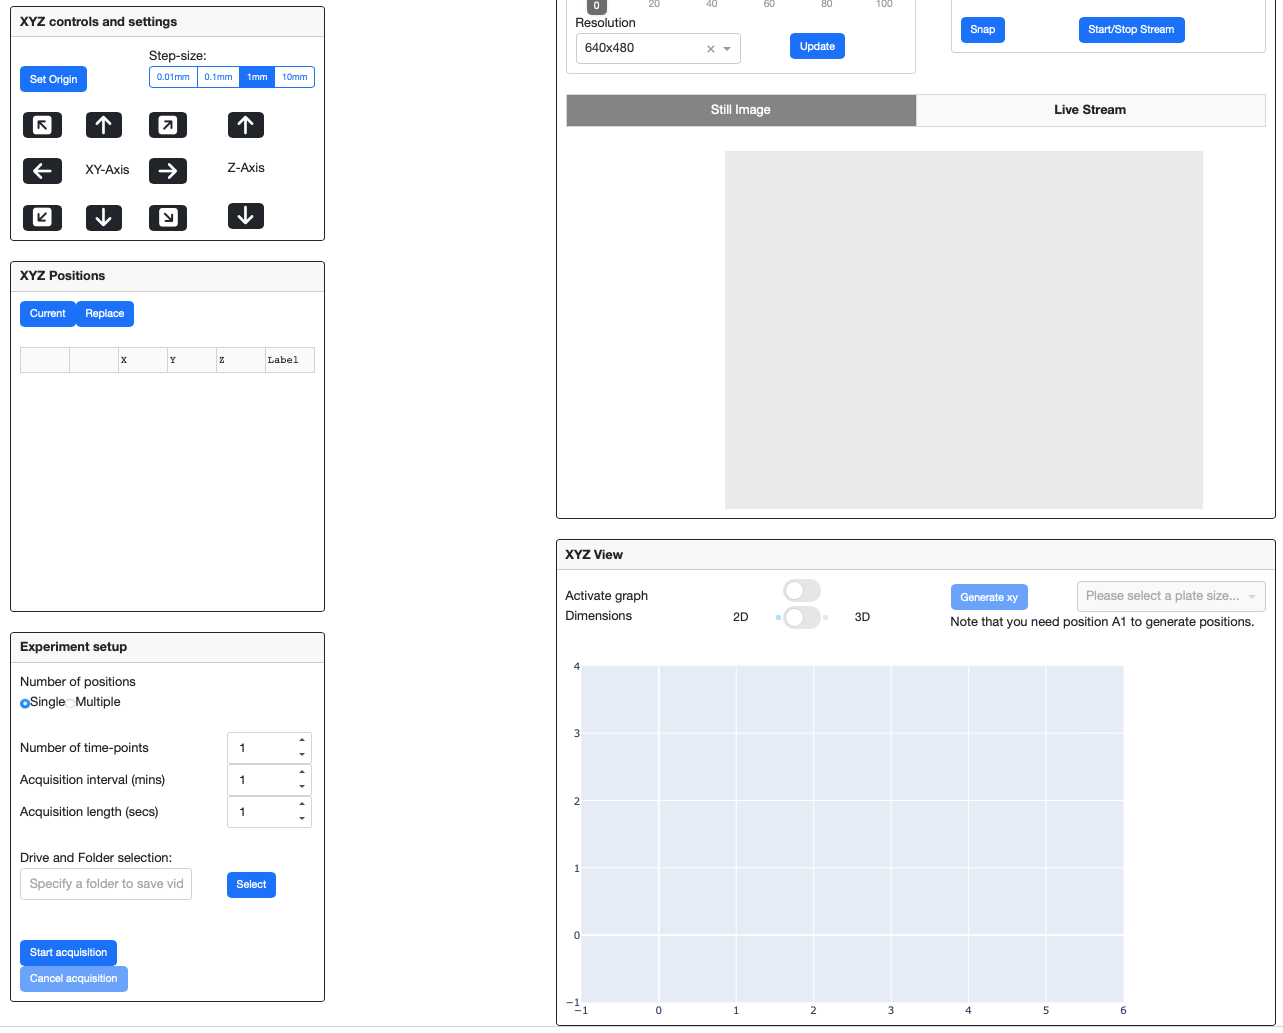
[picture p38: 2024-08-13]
documentation/user_guide/assets/xyz-all.png

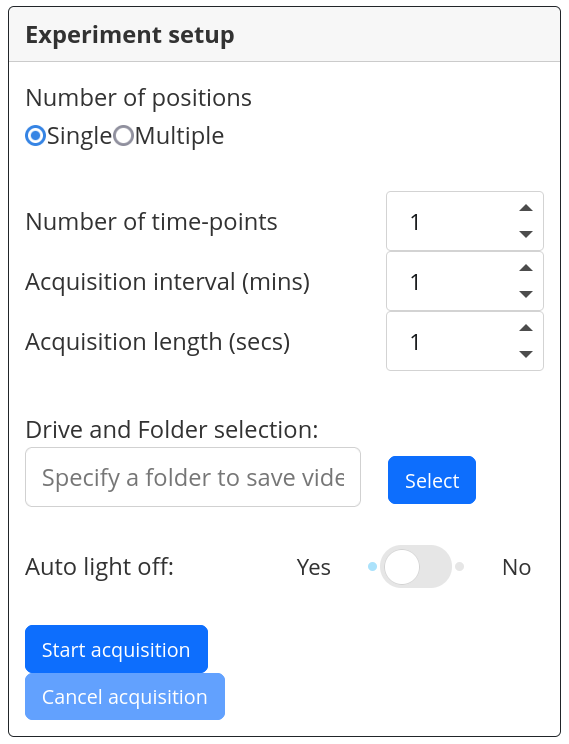
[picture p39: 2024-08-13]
documentation/user_guide/assets/expt-setup.png

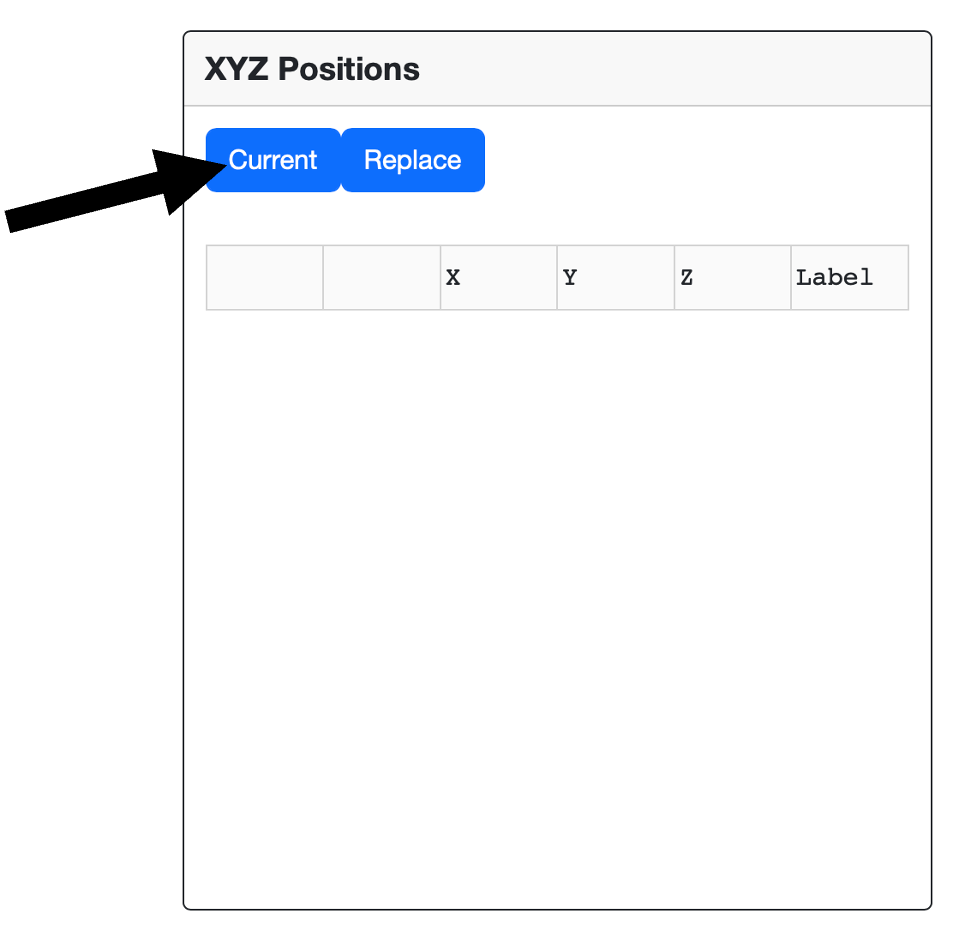
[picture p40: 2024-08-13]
documentation/user_guide/assets/xyz-pos.png

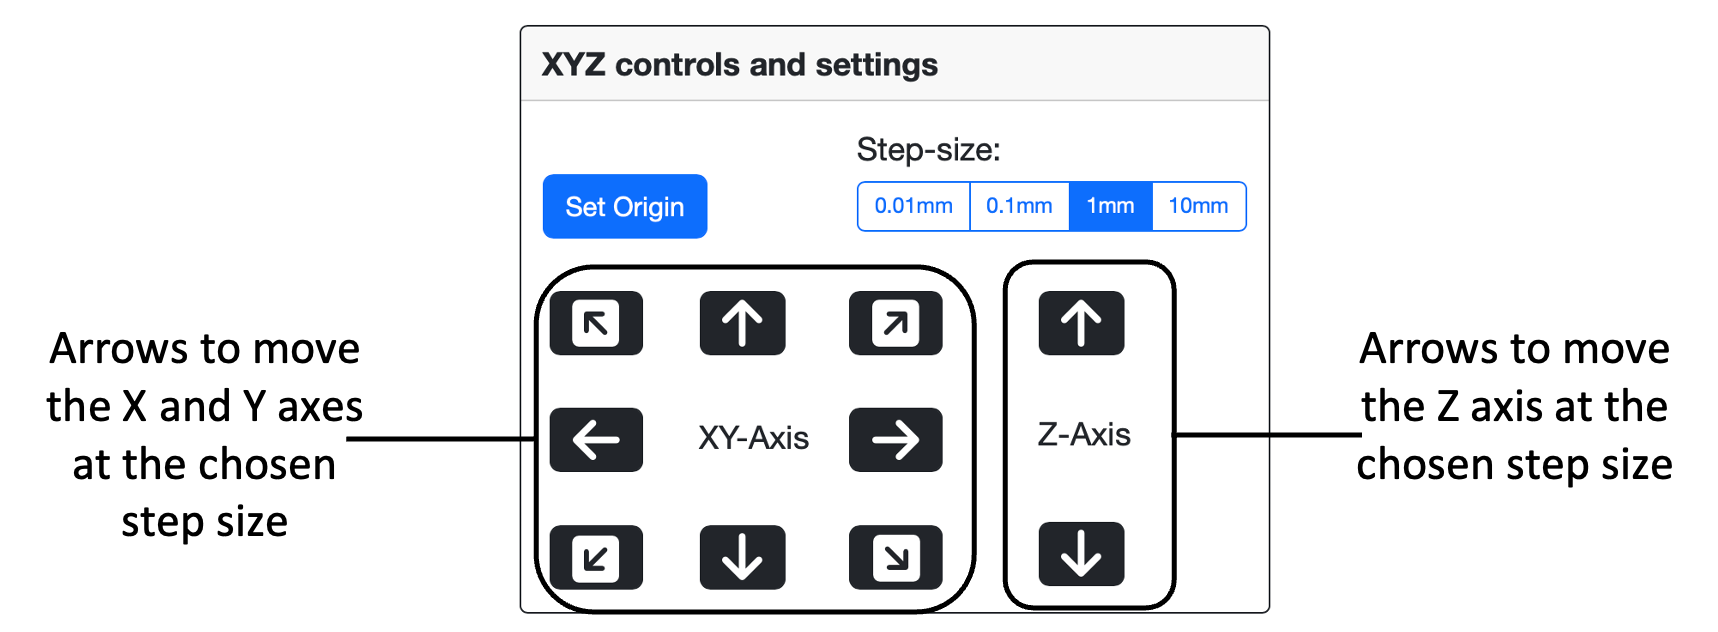
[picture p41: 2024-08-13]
documentation/user_guide/assets/xyz-ctrl.png

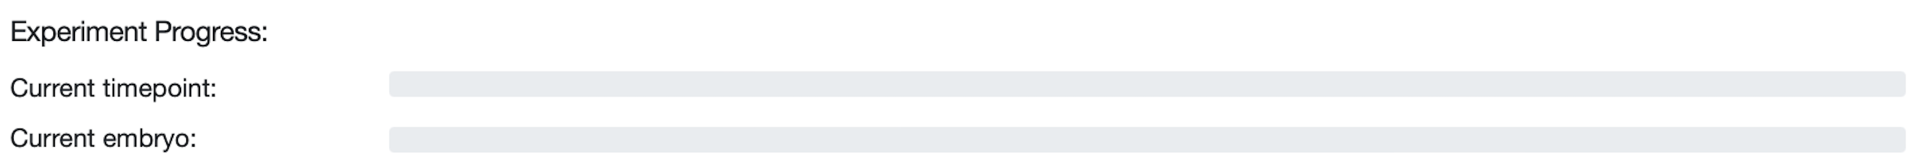
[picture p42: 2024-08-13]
documentation/user_guide/assets/expt-progress.png

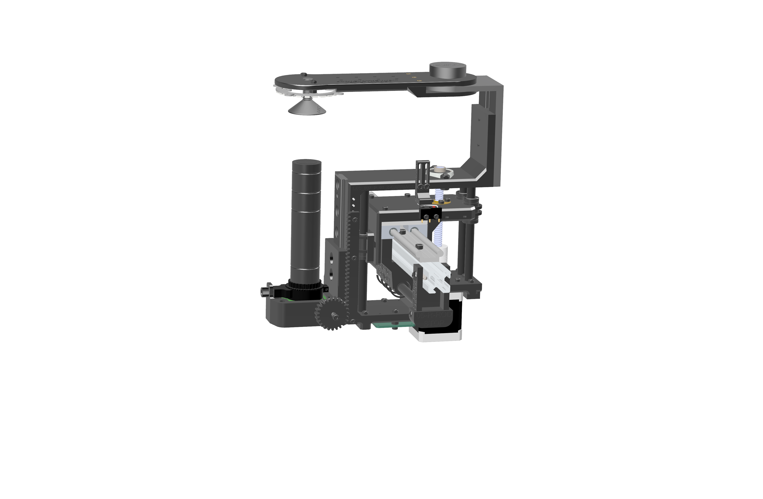
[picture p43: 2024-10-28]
documentation/build_guide/PDFs/Other/FIGURE_6-ANGLED-LEC_007_A_Z-CARRIAGE v39.png

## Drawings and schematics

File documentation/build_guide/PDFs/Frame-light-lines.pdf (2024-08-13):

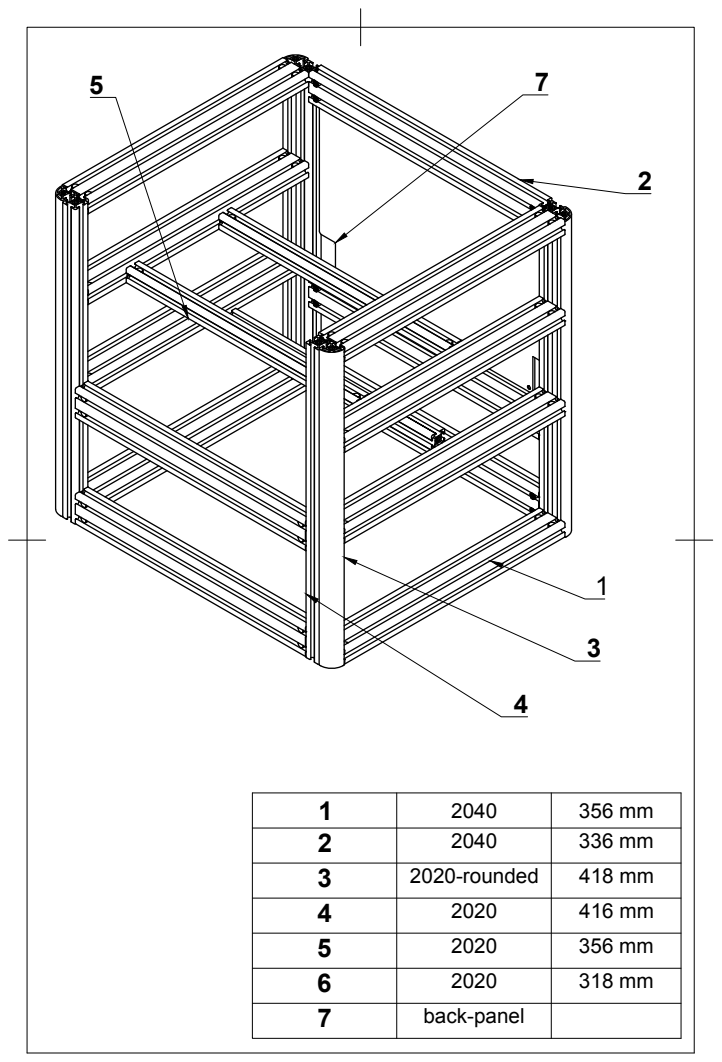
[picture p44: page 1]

1 | 2040 | 356 mm
2 | 2040 | 336 mm
3 | 2020-rounded | 418 mm
4 | 2020 | 416 mm
5 | 2020 | 356 mm
6 | 2020 | 318 mm
7 back-panel

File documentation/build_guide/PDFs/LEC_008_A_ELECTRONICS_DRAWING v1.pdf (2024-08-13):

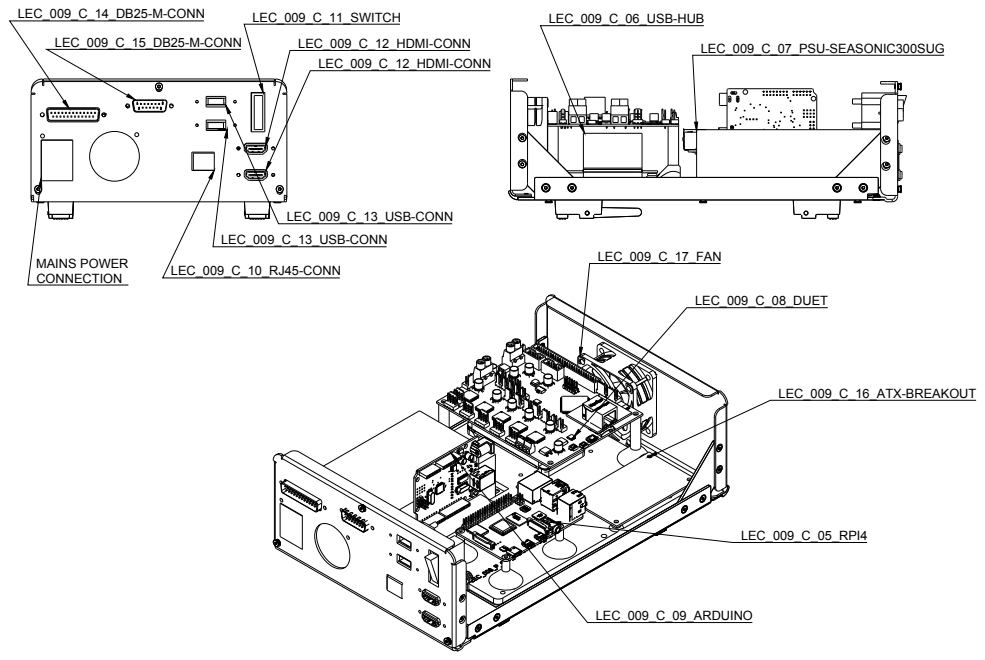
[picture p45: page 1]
MAINS POWER

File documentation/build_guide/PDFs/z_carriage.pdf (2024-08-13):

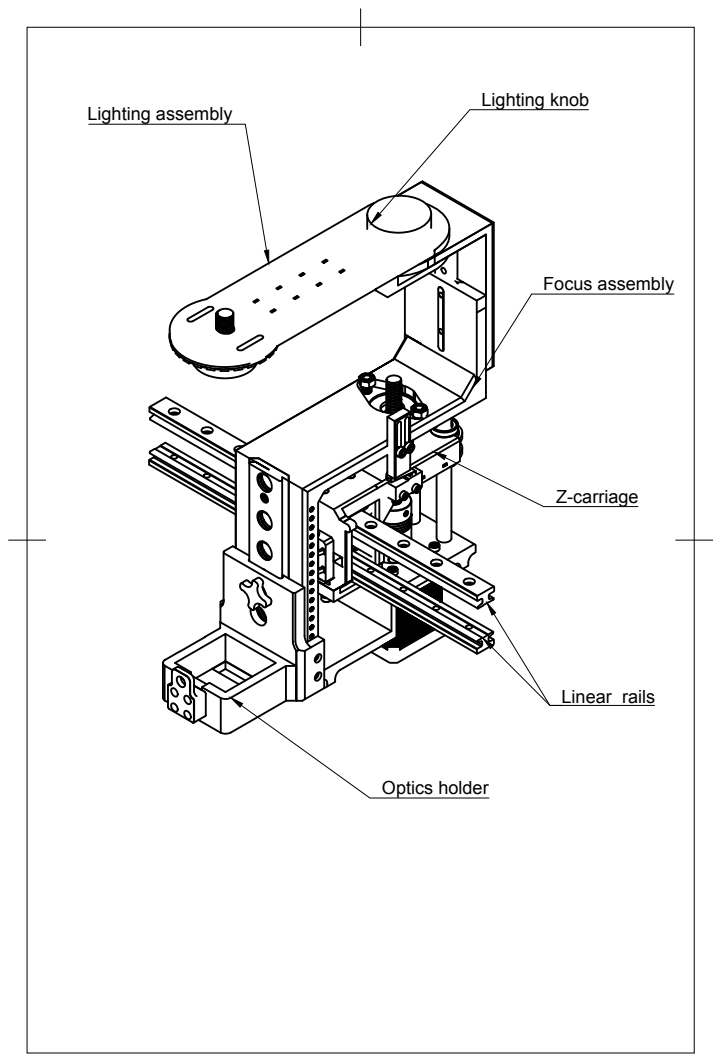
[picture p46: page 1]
Lighting knob; Optics holder; Focus assembly; Linear rails; Lighting assembly

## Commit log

2023-02-02 LED microcontroller code added
2023-02-02 LabEmbryoCam software new file: software/LabEmbryoCam/docs/_static/camera_live_stream_button.png
    [multiwell_24_19.csv, multiwell_384_4.5.csv, multiwell_48_13.csv]
2024-08-13 Consolidating with V2
    [multiwell_24_19.csv, multiwell_384_4.5.csv, multiwell_48_13.csv]
2024-11-18 Update LEC_Build_Guide_Review.md
    Changes to Electronics Section + minor modifications to printed parts table + other sections
2024-11-26 Add change for live optical flow.
2025-01-29 Add V3 support for LED and camera.
